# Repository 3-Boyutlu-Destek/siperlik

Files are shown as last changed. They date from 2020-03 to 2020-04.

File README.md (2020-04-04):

# Yüz Koruyucu Maske (siperlik) Yapımı

Siperlik yapımı için gerekli dosya ve yapım dökümanlarını içerir.

GÜNCELLEME: Lazer kesime ulaşamayan üreticiler için klipsli modeller eklenmiştir.
Klipsli modeller, İstanbul’da üretim yapanlar için değildir. Lazer kesim imkanı olmayan iller içindir.
- Klips_ve_Tac.stl dosyasinda klips ve tac kısmı birliktedir.
- Klips_v2.stl dosyasında sadece klips yer almaktadır.

## Neden Gerekli?

Tıbbi müdahalede buluna personelin başta göz bölgesi olmak üzere yüzünü koruması için bir gözlüğe ihtiyaç duyulmaktadır. Tüm yüzünü damlacıklara karşı korumak için bu dökümanda anlatılan yüz koruyucu maskeye (siperlik) ihtiyaç duyulmaktadır.
CDC (Centers for Disease Control and Prevention) gibi sağlık kuruluşları tarafından gözün ve yüz bölgesinin korunması için önerilmektedir. [1]

## Nasıl Üretirim?

  Tıbbi koruyucu maskenin üretimi sırasıyla 4 aşamadan oluşmaktadır. 
  1) 3B yazıcıdan çıktı alınması
  2) PetG şeffaf plakanın hazırlanması
  3) Esnek lastiğin hazırlanması
  4) Birleştırme

### 1) 3B yazıcıdan çıktı alınması

Üretim için 3B yazıcınızda siperlik_vX.stl dosyasında yer alan modeli bastırmanız gerekmektedir. Alın bandı ve alt takviye tek bir dosyada birleştirilmiştir.

#### Materyal
Öncelikli olarak PLA yoksa ABS ile de baskı alabilirsiniz.

#### Baskı özellikleri

25 Mart 2020 tarihinde güncellenmiştir.

****
- 300 mikron
- 1.2mm duvar kalınlığı
- %25 iç doluluk
- Destek yok
- 100mm/s hız
****

### 2) Şeffaf Plakanın Hazırlanması

A3 ve A4 boyutunda kesilecek PetG materyelin tasarım dosyaları kalkan_A3.dxf ve kalkan_A4.dxf'dir. Tıbbi müdahale ekiplerinden alınan geri bildirim doğrultusunda A3 boyutunu kullanmanız tavsiye edilir. A4 boyutu koruyuculuk açısından yetersiz kalabilmektedir

#### Materyal Özellikleri

0,5 mm PetG

### 3) Esnek Lastik

https://www.tuhafiyecimiz.com/products/copy-of-1-5-cm-yassi-lastik?variant=17374312005

#### Materyel Özellikleri
2 cm genişlikte olmalı

### 4) Nasıl birleştirilir?

Birleştirme aşamaları için rehber.pdf dosyasını inceleyiniz.

https://www.youtube.com/watch?v=pP7z3iw76GA&feature=youtu.be

## Ar-Ge

### Üzerinde çalışılan konu

Şu anda ar-ge ekibi üretimi hızlandıracak bir modeli test etmektedir.

### 3B Baskı

### Model özellikleri

## Kaynaklar
<a id="1">[1]</a> Interim Guidance for Emergency Medical Services (EMS) Systems and 911 Public Safety Answering Points (PSAPs) for COVID-19 in the United States on https://www.cdc.gov/coronavirus/2019-ncov/hcp/guidance-for-ems.html

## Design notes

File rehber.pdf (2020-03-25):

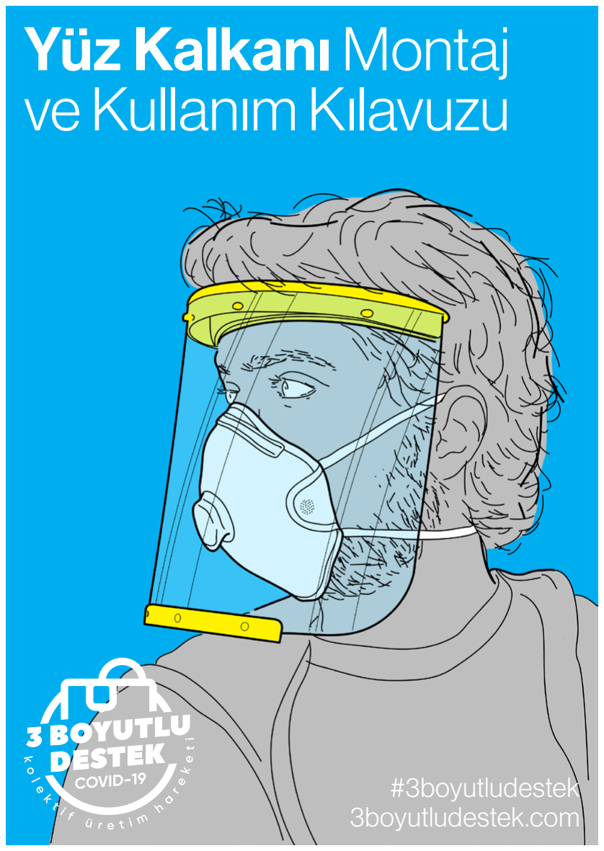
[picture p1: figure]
Yüz Kalkanı Montaj ve Kullanım Kılavuzu; #3boyutludestek 3boyutludestek.com
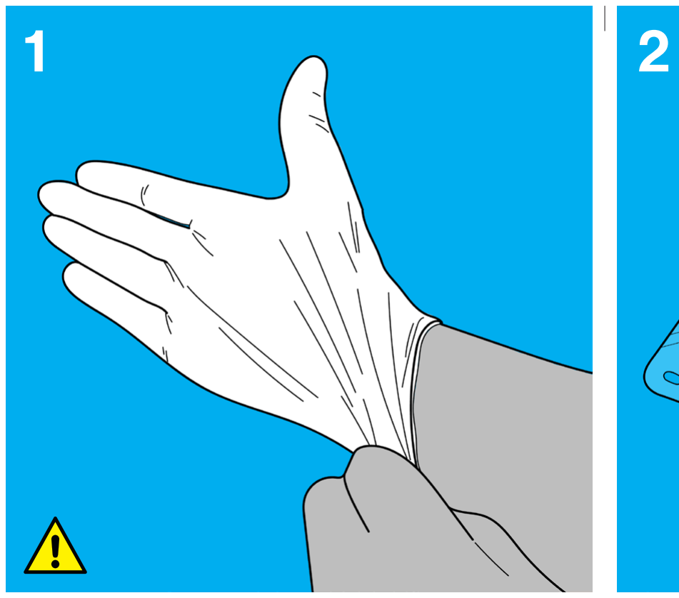
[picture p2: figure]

TEMİZ ÇALIŞMA ORTAMI: Montaj ortamının temiz olması gerekmektedir. DEZENFEKSİYON: Montaj öncesinde ellerinizi dezenfekte edin. Mümkünse temiz eldivenler kullanın. STERİLİZASYON: Ürünün steril olmadığını unutmayın, montajdan sonra sterilize edin.

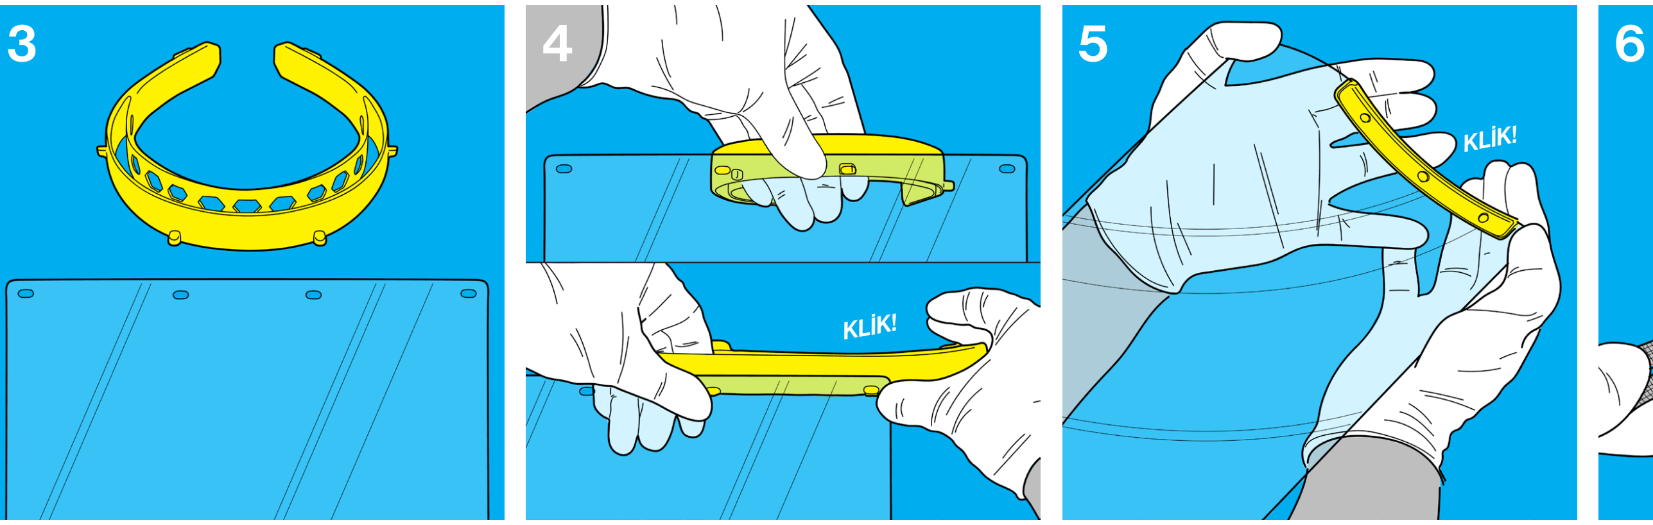
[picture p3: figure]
KLİK!
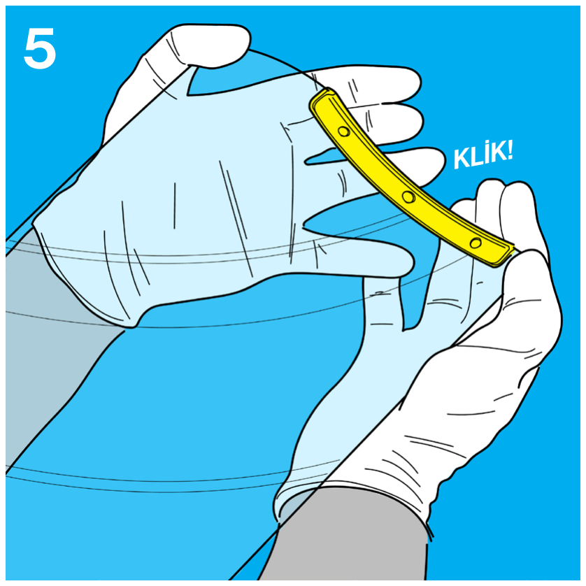
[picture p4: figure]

Şeffaf Kalkan³ ile Üst Parça¹’nın birleşim noktasını karnınıza veya başka bir sert yüzeye yaslayın. Şeffaf Kalkan³’ın açıktaki ve üç delikli tarafına, Alt Parça²’yı dış tarafta kalacak şekilde yerleştirin. Yerleştiğinde bir “klik” sesi duyacaksınız. Alt Parça²’nın iyice yerleştiğinden emin olun, Şeffaf Kalkan³ ile aralarında boşluk kalmamalıdır.

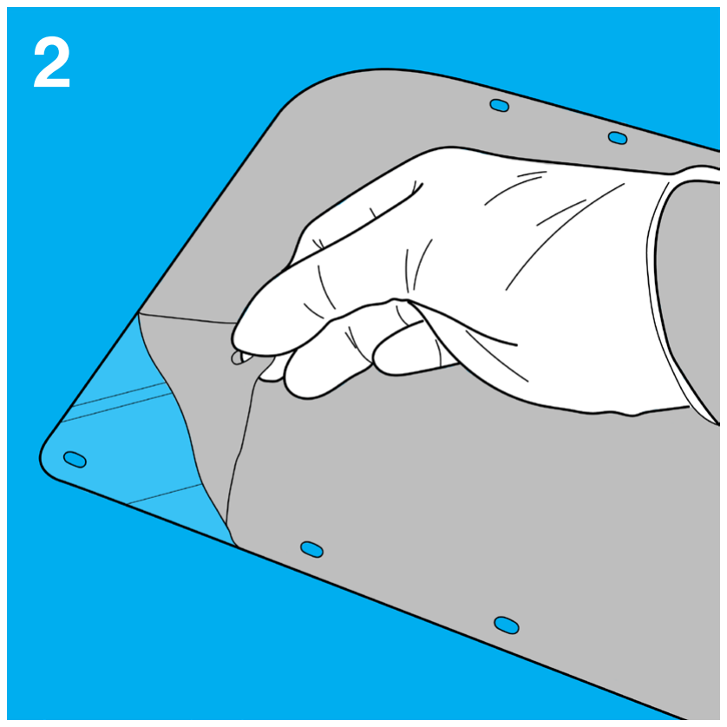
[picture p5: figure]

Şeffaf Kalkan³’ın iki tarafı da koruma filmi ile kaplıdır. Koruma filmlerini köşelerinden başlayarak çıkarın.

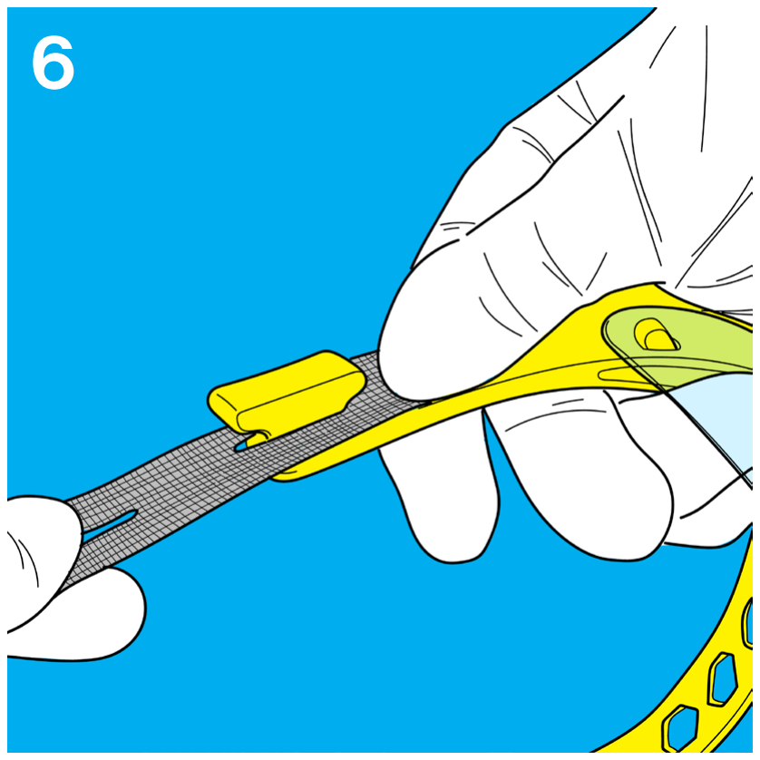
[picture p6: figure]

Elastik Bant⁴’ın herhangi bir tarafındaki deliği, Üst Parça¹’nın iki ucunda da bulunan çıkıntıların birinden geçirin. Aynısını diğer uç için de uygulayın. Gerekli durumlarda başınıza göre ayarlayın. Yüz Kalkanı’nız hazır! Kullanmadan önce ürünün tüm yüzeylerini dezenfekte etmeyi unutmayın.

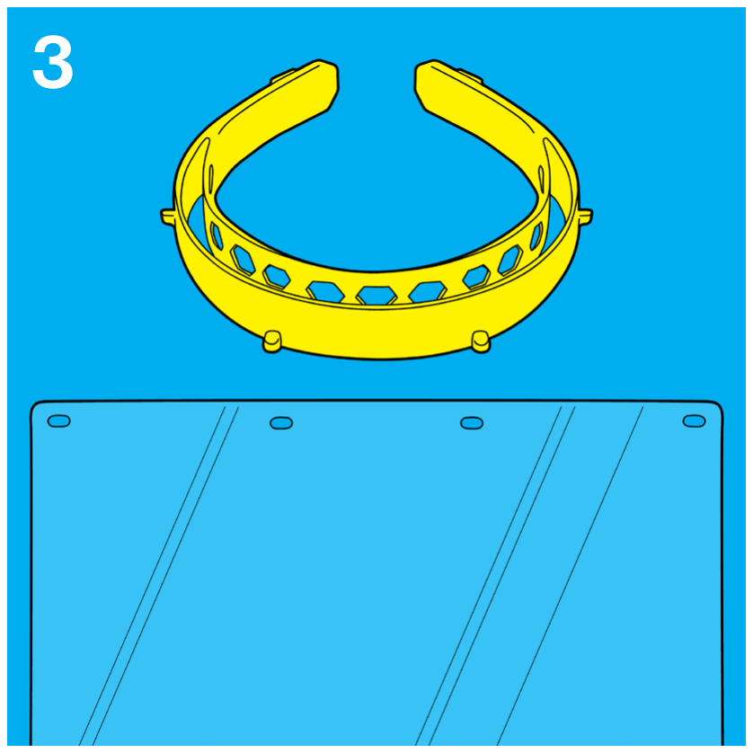
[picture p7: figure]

Şeffaf Kalkan³’ı dört delikli tarafı üstte olacak şekilde tutun. Üst Parça¹’yı üzerindeki dört çıkıntı altta kalacak şekilde tutun.

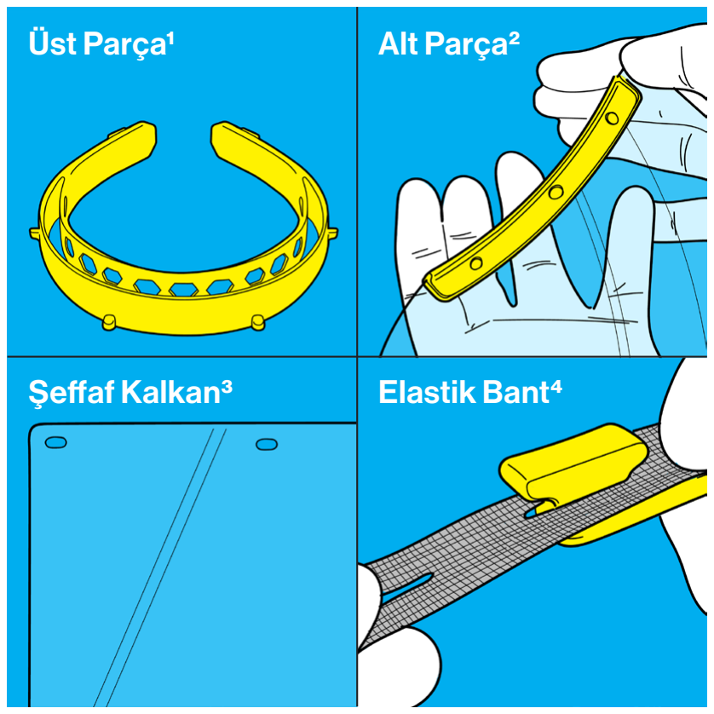
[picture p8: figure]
Üst Parça¹; Şeffaf Kalkan³; Alt Parça²; Elastik Bant⁴

Bu kılavuz, Yüz
Kalkanı’nızı bir
araya getirirken size
yol göstermesi için
hazırlanmıştır. Lütfen
uyarıları dikkate alın.

PARÇALAR:
1 adet Üst Parça¹ (Alın)
1 adet Alt Parça² (Çene)
1 adet Şeffaf Kalkan³
1 adet Elastik Bant⁴

Şeffaf Kalkan³’daki sağdan ikinci delik ile Üst Parça¹’daki sağdan ikinci çıkıntıyı eşleştirin. Çıkıntıyı delikten geçirdikten sonra bir elinizle sabit tutup,
en sağdaki delik ve çıkıntıyı eşleştirin. Parçalar yerleştiğinde bir “klik” sesi duyacaksınız. Aynısını sol taraf için de tekrarlayın. Şeffaf Kalkan³’ı fazla
Kılavuz Tasarımı: Ufuk Barış Mutlu Metin: Deniz Uçan | bükmemeye özen gösterin.

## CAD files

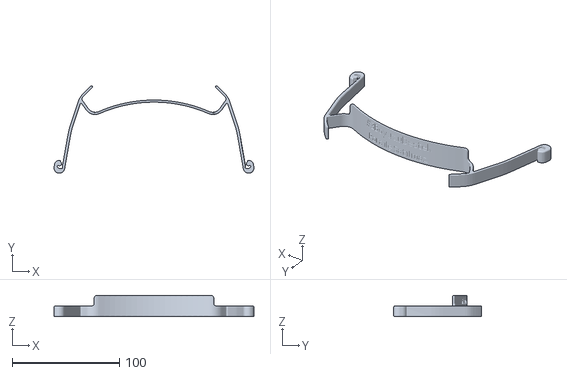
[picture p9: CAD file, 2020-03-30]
Siperlik_Tac_Klipsli.stl
186.3 x 81.5 x 20.0

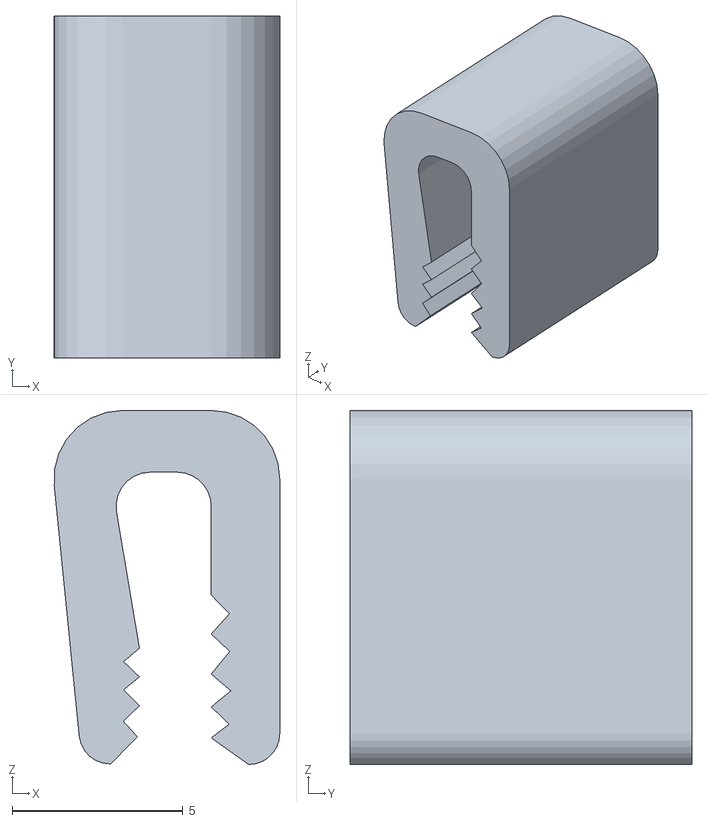
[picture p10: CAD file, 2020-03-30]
Klips_V2.stl
6.60 x 10.0 x 10.4

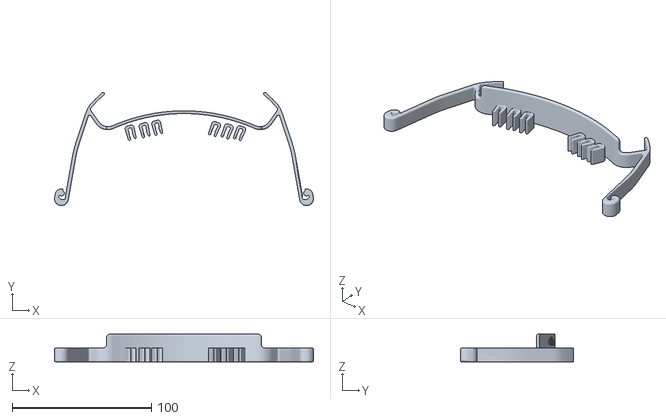
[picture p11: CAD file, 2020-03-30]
Siperlik_Klips_ve_Tac.stl
186.3 x 81.5 x 20.0

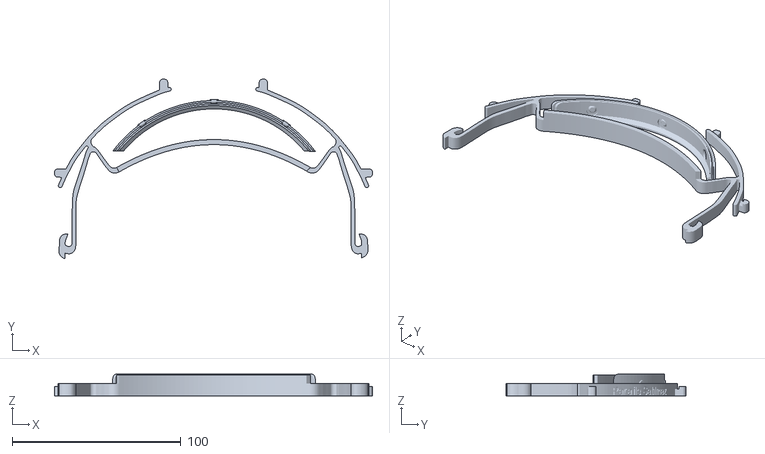
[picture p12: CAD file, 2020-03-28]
siperlik_v4_1.stl
188.5 x 106.5 x 13.0

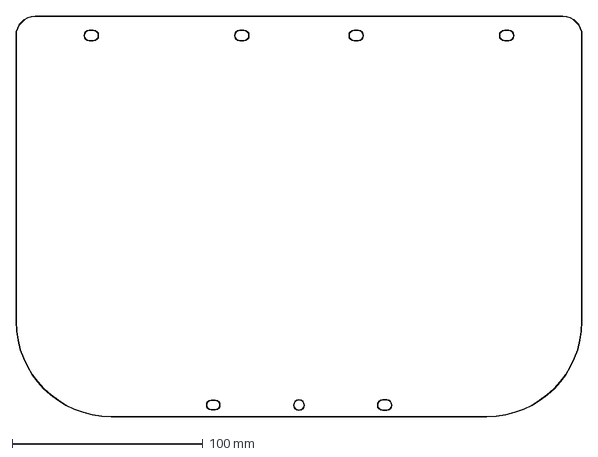
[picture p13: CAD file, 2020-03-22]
kalkan_A4.dxf
297.0 x 210.0 mm

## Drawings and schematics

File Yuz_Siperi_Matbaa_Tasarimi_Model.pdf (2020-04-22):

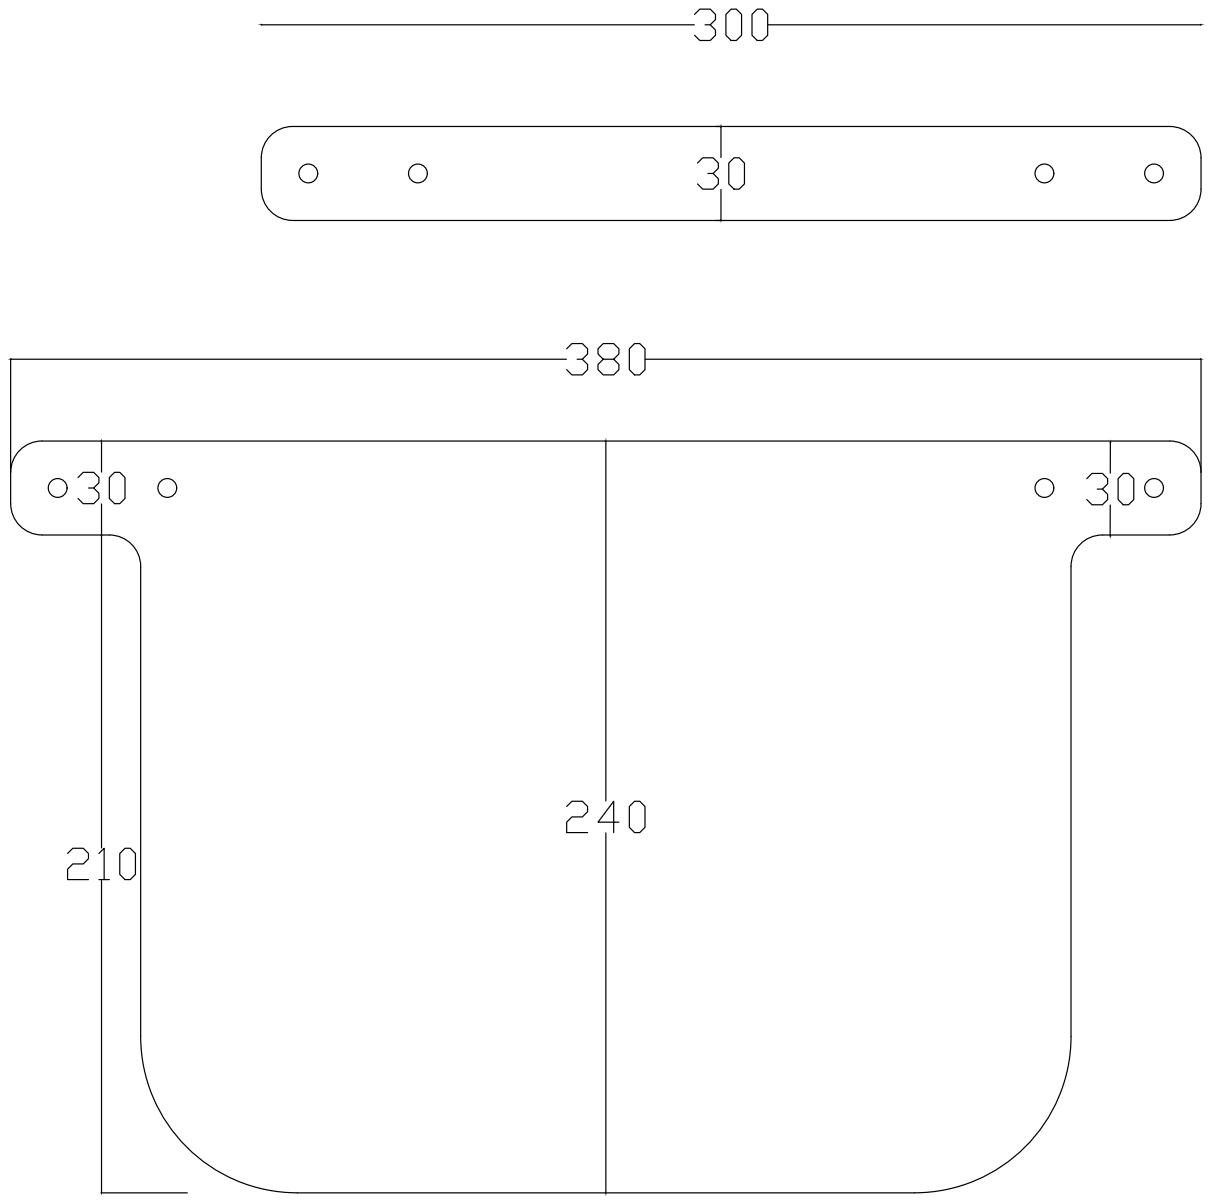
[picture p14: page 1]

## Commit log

2020-03-23 Yeni model eklendi. \n Eski model arşivlendi. \n Döküman güncellendi.
    [alin_bandi_r1.stl, alt_takviye.stl, covid19_headband_rc2.stl]
2020-03-23 Notasyon ve isimlendirme hataları düzeltildi.
    [alinBandi_ve_takviye_r1.stl, bottom_reinforcement.stl]
2020-03-23 Yuz Kalkani_2 Saat_PARA ILE SATILAMAZ
    [yuz kalkanı.stl]
2020-03-23 Organizasyon sorunları giderildi.
    [bottom_reinforcement.stl, covid19_headband_rc2.stl, yuz kalkanı.stl]
2020-03-23 dosyalar güncellendi.
    [alinBandi_ve_takviye_r1.stl, shield_final_A3.dxf, shield_final_A4.dxf]
2020-03-23 döküman ve isimler güncellendi.
    [kalkan_A3.dxf, kalkan_A4.dxf]
2020-03-23 isim düzenleme
    [siperlik.stl]
2020-03-23 altıgen yapılar kaldırıldı.
    [siperlik_v2.stl]
2020-03-25 eski versiyonlar yanlış üretimin önüne geçmek için kaldırıldı.
    [siperlik.stl, siperlik_v2.stl]
2020-03-25 Üretim süresi daha kısa olan model eklendi.
    [siperlik_v3.stl]
2020-03-27 Sizi seviyoruz yazısı eklendi.
    [siperlik_v3.stl, siperlik_v4.stl]
2020-03-28 Gelen sikayetler üzerine tırnaklar kalınlastırıldı.
    [siperlik_v4.stl, siperlik_v4_1.stl]
2020-03-30 Klipsli modeller eklendi.
    [Klips_V2.stl, Siperlik_Klips_ve_Tac.stl, Siperlik_Tac_Klipsli.stl]
